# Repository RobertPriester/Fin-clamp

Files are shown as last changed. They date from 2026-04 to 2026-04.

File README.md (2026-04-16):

# Juvenile Fin-Clamp: Open hardware designs, sensor processing scripts and CFD resources for minimally invasive biologging of juvenile sharks

This repository contains all hardware design files, sensor processing scripts, 
and computational fluid dynamics (CFD) resources associated with the following publication:

> Citation and DOI to be added upon publication.

## Repository Structure

### 🗂️ Fin-clamp production
Resources to reproduce the Juvenile Fin-Clamp hardware.
- **CAD resources** — CAD files in .step (universal) and .f3z (Fusion 360) formats
- **Instructions** — Step-by-step production instructions, PDF technical plans and assembly resources

### 📊 Sensor processing scripts
R scripts for processing LittleLeonardo accelerometry, depth and temperature data 
to reproduce the results of the publication. Includes an R script adapted from the 
MATLAB code of Cade et al. (2018) to run jiggle method calculations.

### 🌊 CFD
Resources for the computational fluid dynamics simulations.
- **3D models** — Simplified .stl models of the Juvenile Fin-Clamp and juvenile 
  smooth hammerhead shark used in SimScale simulations
- **Simulation results** — SimScale simulation outputs, summary table, and R scripts 
  for processing results and producing figures

## Authors

C. Robert Priester, Jorge Fontes, Fred Buyle, Diya Das, Bruno C. L. Macena, 
Colin Simpfendorfer, Esben Moland Olsen, Pedro Afonso

## Software Requirements

### R Scripts
The sensor processing and CFD result scripts were developed in R. We recommend 
using a recent version of R (≥ 4.0) and RStudio. Required packages are listed 
at the top of each script. The jiggle method script is adapted from the original 
MATLAB code of Cade et al. (2018) for use in R.

> Cade, D.E., Barr, K.R., Calambokidis, J., Friedlaender, A.S. and Goldbogen, J.A. 
> (2018). Determining forward speed from accelerometer jiggle in aquatic 
> environments. Journal of Experimental Biology, 221(2).

### CFD Simulations
Simulations were run using [SimScale](https://www.simscale.com/), a web-based 
CFD platform. The .stl files in the /CFD/3D models folder can be imported 
directly into SimScale to reproduce or modify the simulations.

## Data Availability

Raw tag data used and analyzed in this study are not publicly archived due to 
ongoing research but are available from the corresponding author upon reasonable 
request.

## License

Hardware design files (CAD, production files): CERN Open Hardware Licence v2 - Strongly Reciprocal (CERN-OHL-S v2) 
Documentation and instructions: Creative Commons Attribution 4.0 International (CC BY 4.0)

## Contact

**C. Robert Priester** (corresponding author)
robert.priester@posteo.de

For questions related to fin-clamp development and contributions, please use 
the [GitHub Issues](../../issues) function of this repository.

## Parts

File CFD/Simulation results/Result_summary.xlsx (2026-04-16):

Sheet: Meta
Run | Shark_size | Weight | Tag/Shark_weight | Tag/shark_area | Tag | Tag_weight | Tag_frontal_area | Velocity | Ref_area | Cells | Quality | Iteration
120_0.5_NA | 1.2 | 8470.56 | 1.2% | 10.9% | NO | 100 | 0.00157084 | 0.5 | 0.01446 | 6110226 | 0.576 | 2000
120_0.5_T | 1.2 | 8470.56 | 1.2% | 10.9% | YES | 100 | 0.00157084 | 0.5 | 0.01446 | 3933008 | 0.384 | 2000
80_1_NA | 0.8 | 2624.27 | 3.8% | 16.3% | NO | 100 | 0.00157084 | 1 | 0.00964 | 5966981 | 0.585 | 2000
100_1_NA | 1 | 5001.24 | 2.0% | 13.0% | NO | 100 | 0.00157084 | 1 | 0.01205 | 6742979 | 0.556 | 2000
120_1_NA | 1.2 | 8470.56 | 1.2% | 10.9% | NO | 100 | 0.00157084 | 1 | 0.01446 | 6110393 | 0.576 | 2000
160_1_NA | 1.6 | 19452.92 | 0.5% | 8.2% | NO | 100 | 0.00157084 | 1 | 0.01927 | 4154136 | 0.501 | 2000
80_1_T | 0.8 | 2624.27 | 3.8% | 16.3% | YES | 100 | 0.00157084 | 1 | 0.00964 | 4520569 | 0.494 | 2000
100_1_T | 1 | 5001.24 | 2.0% | 13.0% | YES | 100 | 0.00157084 | 1 | 0.01205 | 4726084 | 0.502 | 2000
120_1_T | 1.2 | 8470.56 | 1.2% | 10.9% | YES | 100 | 0.00157084 | 1 | 0.01446 | 3934513 | 0.389 | 2000
160_1_T | 1.6 | 19452.92 | 0.5% | 8.2% | YES | 100 | 0.00157084 | 1 | 0.01927 | 3469121 | 0.417 | 2000
80_2.5_NA | 0.8 | 2624.27 | 3.8% | 16.3% | NO | 100 | 0.00157084 | 2.5 | 0.00964 | 5966851 | 0.583 | 2000
120_2.5_NA | 1.2 | 8470.56 | 1.2% | 10.9% | NO | 100 | 0.00157084 | 2.5 | 0.01446 | 6110393 | 0.576 | 2000
160_2.5_NA | 1.6 | 19452.92 | 0.5% | 8.2% | NO | 100 | 0.00157084 | 2.5 | 0.01927 | 4154136 | 0.501 | 2000
80_2.5_T | 0.8 | 2624.27 | 3.8% | 16.3% | YES | 100 | 0.00157084 | 2.5 | 0.00964 | 4520569 | 0.494 | 2000
120_2.5_T | 1.2 | 8470.56 | 1.2% | 10.9% | YES | 100 | 0.00157084 | 2.5 | 0.01446 | 3934513 | 0.389 | 2000
160_2.5_T | 1.6 | 19452.92 | 0.5% | 8.2% | YES | 100 | 0.00157084 | 2.5 | 0.01927 | 3469121 | 0.417 | 2000

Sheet: Simulations
Run | Shark size | Weight | Tag/Shark weight | Tag/shark area | Tag | Tag weight | Tag frontal area | Velocity(m/s) | Reference area | Cells | Quality | Iteration | PRESSURE_FORCE_X | PRESSURE_FORCE_Y | PRESSURE_FORCE_Z | TOTAL_FORCE_X | TOTAL_FORCE_Y | TOTAL_FORCE_Z | VISCOUS_FORCE_X | VISCOUS_FORCE_Y | VISCOUS_FORCE_Z | Delta_Total_X |  | Delta_power | Metabolic_energy_W | Metabolic_energy_J | Daily_energy_penalty
120_0.5_NA | 1.2 | 8470.56 | 1.2% | 10.9% | NO | 105 | 0.00157084 | 0.5 | 0.01446 | 6110226 | 0.576 | 2000 | 0.40 | 0.05 | 1.89 | 0.71 | 0.05 | 1.87 | 0.31 | 0.002039952769 | -0.02 | 0.04 | 5.58%
120_0.5_T | 1.2 | 8470.56 | 1.2% | 10.9% | YES | 105 | 0.00157084 | 0.5 | 0.01446 | 3933008 | 0.384 | 2000 | 0.44 | 0.14 | 1.91 | 0.75 | 0.14 | 1.89 | 0.31 | 0.0005188760977 | -0.02
80_1_NA | 0.8 | 2624.27 | 4.0% | 16.3% | NO | 105 | 0.00157084 | 1 | 0.00964 | 5966981 | 0.585 | 2000 | 0.70 | 0.07 | 3.42 | 1.22 | 0.07 | 3.38 | 0.52 | 0.001136633648 | -0.04 | 5.8440 | 477.74%
100_1_NA | 1 | 5001.24 | 2.1% | 13.0% | NO | 105 | 0.00157084 | 1 | 0.01205 | 6742979 | 0.556 | 2000 | 1.03 | -0.06 | 5.53 | 1.83 | -0.06 | 5.47 | 0.80 | 0.002823207532 | -0.06
120_1_NA | 1.2 | 8470.56 | 1.2% | 10.9% | NO | 105 | 0.00157084 | 1 | 0.01446 | 6110393 | 0.576 | 2000 | 1.55 | 0.23 | 7.87 | 2.67 | 0.23 | 7.78 | 1.12 | 0.01 | -0.09 | 12.7556 | 478.30%
160_1_NA | 1.6 | 19452.92 | 0.5% | 8.2% | NO | 105 | 0.00157084 | 1 | 0.01927 | 4154136 | 0.501 | 2000 | 2.60 | -0.01 | 14.16 | 4.53 | -0.0009062607321 | 14.01 | 1.94 | 0.01 | -0.15 | 21.6252 | 477.07%
80_1_T | 0.8 | 2624.27 | 4.0% | 16.3% | YES | 105 | 0.00157084 | 1 | 0.00964 | 4520569 | 0.494 | 2000 | 1.02 | 0.56 | 3.42 | 1.56 | 0.56 | 3.38 | 0.53 | -0.001440980359 | -0.04 | 0.3323 | 27.16% | 0.3322642967 | 1.329057187 | 4784.605872 | 114.8 | -0.5660293074 | -0.09691001301
100_1_T | 1 | 5001.24 | 2.1% | 13.0% | YES | 105 | 0.00157084 | 1 | 0.01205 | 4726084 | 0.502 | 2000 | 1.42 | 0.60 | 5.51 | 2.21 | 0.60 | 5.45 | 0.78 | -0.00194117961 | -0.06 | 0.3813 | 20.87%
120_1_T | 1.2 | 8470.56 | 1.2% | 10.9% | YES | 105 | 0.00157084 | 1 | 0.01446 | 3934513 | 0.389 | 2000 | 1.71 | 0.54 | 7.86 | 2.82 | 0.54 | 7.77 | 1.11 | -0.0005802425074 | -0.09 | 0.1564 | 5.87% | 0.1564333467 | 0.6257333866 | 2252.640192 | 54.1 | -1.231669021 | 0.07918124605
160_1_T | 1.6 | 19452.92 | 0.5% | 8.2% | YES | 105 | 0.00157084 | 1 | 0.01927 | 3469121 | 0.417 | 2000 | 2.82 | 0.74 | 14.13 | 4.73 | 0.74 | 13.97 | 1.91 | 0.01 | -0.16 | 0.2021 | 4.46% | 0.2021191677 | 0.808476671 | 2910.516016 | 69.9 | -1.350765638 | 0.2041199827
80_2.5_NA | 0.8 | 2624.27 | 4.0% | 16.3% | NO | 105 | 0.00157084 | 2.5 | 0.00964 | 5966851 | 0.583 | 2000 | 4.17 | 0.64 | 22.20 | 7.07 | 0.64 | 21.98 | 2.89 | 0.003504137696 | -0.22 | 7.66 | 492.17%
120_2.5_NA | 1.2 | 8470.56 | 1.2% | 10.9% | NO | 105 | 0.00157084 | 2.5 | 0.01446 | 6110393 | 0.576 | 2000 | 9.28 | 1.96 | 50.73 | 15.42 | 1.98 | 50.26 | 6.14 | 0.02 | -0.47 | 13.54 | 479.72%
160_2.5_NA | 1.6 | 19452.92 | 0.5% | 8.2% | NO | 105 | 0.00157084 | 2.5 | 0.01927 | 4154136 | 0.501 | 2000 | 15.68 | -0.15 | 90.19 | 26.16 | -0.12 | 89.41 | 10.48 | 0.03 | -0.77 | 22.63 | 478.00%
80_2.5_T | 0.8 | 2624.27 | 4.0% | 16.3% | YES | 105 | 0.00157084 | 2.5 | 0.00964 | 4520569 | 0.494 | 2000 | 6.25 | 3.41 | 21.86 | 9.21 | 3.40 | 21.63 | 2.96 | -0.01 | -0.22 | 2.1441 | 30.34% | 5.360261068 | 21.44104427 | 77187.75938 | 1852.5
120_2.5_T | 1.2 | 8470.56 | 1.2% | 10.9% | YES | 105 | 0.00157084 | 2.5 | 0.01446 | 3934513 | 0.389 | 2000 | 10.31 | 3.42 | 50.33 | 16.37 | 3.41 | 49.86 | 6.06 | -0.01 | -0.47 | 0.9446 | 6.12% | 2.361517566 | 9.446070262 | 34005.85294 | 816.1
160_2.5_T | 1.6 | 19452.92 | 0.5% | 8.2% | YES | 105 | 0.00157084 | 2.5 | 0.01927 | 3469121 | 0.417 | 2000 | 17.05 | 3.96 | 89.98 | 27.37 | 3.98 | 89.15 | 10.32 | 0.02 | -0.83 | 1.2103 | 4.63% | 3.02571437 | 12.10285748 | 43570.28693 | 1045.7
 |  |  |  |  |  |  |  |  |  |  |  |  |  |  |  |  |  |  |  |  |  |  |  |  | 111.6935848601%
 |  |  |  |  |  |  |  |  |  |  |  |  |  |  |  |  |  |  |  |  |  |  |  |  | 103.7644536316%

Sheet: Mesh dependancy
Run | Input mesh | Shark size | Tag | Velocity(m/s) | Algorithm | Fineness | Volumes | Nodes | Max NonO | Quality score | PRESSURE_FORCE_X | PRESSURE_FORCE_Y | PRESSURE_FORCE_Z | TOTAL_FORCE_X | TOTAL_FORCE_Y | TOTAL_FORCE_Z | VISCOUS_FORCE_X | VISCOUS_FORCE_Y | VISCOUS_FORCE_Z | Column1
Pre | Remodelled251023_remeshed_reducedIII | 80 | NO | 1 | Hex | Fine | 1540100 | 2088741 | 87.97 | 0.46 | 0.90 | -0.23 | 3.27 | 1.45 | -0.23 | 3.24 | 0.55 | 0.0006168922828 | -0.04
Pre | Remodelled241030_reduced50 | 80 | NO | 1 | Hex | Moderate | 1979896 | 2376287 | 87.85 | 0.52 | 1.09 | 0.04 | 3.58 | 1.65 | 0.04 | 3.55 | 0.56 | 0.002417378538 | -0.03
Pre | Remodelled251023_remeshed_reducedIII | 80 | NO | 1 | Standard | 5 | 3555913 | 989374 | 89.1 |  | 0.95 | -0.09 | 3.64 | 1.46 | -0.09 | 3.61 | 0.51 | 0.0006941273648 | -0.03
Pre | Remodelled241030_reduced50 | 80 | NO | 1 | Hex | Fine | 4103420 | 4852123 | 85.7 | 0.54 | 0.89 | -0.02 | 3.72 | 1.44 | -0.02 | 3.69 | 0.54 | 0.001064137875 | -0.04
Manual | Remodelled241030_reduced50 | 80 | NO | 1 | Hex | Manual (0.5) | 7657633 | 10124840 | 86.56 | 0.59 | 0.71 | 0.01 | 3.38 | 1.23 | 0.01 | 3.34 | 0.52 | 0.002300590639 | -0.04 | 0.00
Manual | Remodelled241030_reduced50 | 80 | NO | 1 | Hex | Manual (0.65) | 5966981 | 7764503 | 85.44 | 0.59 | 0.70 | 0.07 | 3.42 | 1.22 | 0.07 | 3.38 | 0.52 | 0.001136321584 | -0.04 | 0.01
Manual | Remodelled241030_reduced50 | 80 | NO | 1 | Hex | Manual (0.725) | 2995024 | 3872601 | 87.35 | 0.5 | 0.73 | -0.04 | 3.46 | 1.25 | -0.03 | 3.42 | 0.52 | 0.002223197654 | -0.04 | -0.02
Manual | Remodelled241030_reduced50 | 80 | NO | 1 | Hex | Manual (5) | 1253214 | 1445283 | 87.11 | 0.61 | 1.14 | 0.01 | 3.40 | 1.66 | 0.01 | 3.38 | 0.52 | 0.0008462221316 | -0.02 | -0.42
Manual | Remodelled241030_reduced50 | 80 | NO | 1 | Hex | Manual (12) | 643259 | 728039 | 87.38 | 0.64 | 1.63 | -0.14 | 3.89 | 2.14 | -0.14 | 3.86 | 0.51 | -0.0006558393983 | -0.03 | -0.49
Manual | Remodelled241030_reduced50 | 80 | NO | 1 | Hex | Manual (15) | 394268 | 468042 | 87.53 | 0.57 | 1.42 | 0.01 | 2.88 | 1.89 | 0.02 | 2.86 | 0.47 | 0.004983145064 | -0.02 | 0.21

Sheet: Sheet1
Run | Shark size | Tag | Velocity(m/s) | Vol_Xfront | Vol_Xback | Vol_Y | Vol_Z | Reference length | Reference area |  |  | Scaling
1 | 0.8 | NO | 1 | 4 | 8 | 1.1 | 1.1 | 0.8 | 0.009637 |  |  |  | TL | Cephalofoil | Ratio
4 | 0.8 | YES | 1 | 4 | 8 | 1.1 | 1.1 | 0.8 | 0.01204625
7 | 0.8 | NO | 3 | 4 | 8 | 1.1 | 1.1 | 0.8 | 0.0144555 |  | 592.7 | 800 | 125.8 | 34.3 | 0.2726550079
10 | 0.8 | YES | 3 | 4 | 8 | 1.1 | 1.1 | 0.8 | 0.019274 |  | Scaling original to 800 | 1.350
 | 1 | YES | 1 | 5 | 10 | 1.4 | 1.4 | 1 |  |  | 100 | 1.687
 | 1 | NO | 2 | 5 | 10 | 1.4 | 1.4 | 1 |  |  | Scaling 120 | 2.02
2 | 1.2 | NO | 1 | 6 | 12 | 1.6 | 1.6 | 1.2 |  |  | Scaling 160 | 2.70
5 | 1.2 | YES | 1 | 6 | 12 | 1.6 | 1.6 | 1.2 | 0.020362393
8 | 1.2 | NO | 3 | 6 | 12 | 1.6 | 1.6 | 1.2
11 | 1.2 | YES | 3 | 6 | 12 | 1.6 | 1.6 | 1.2
3 | 1.6 | NO | 1 | 8 | 16 | 2.2 | 2.2 | 1.6 | 0.020362393
6 | 1.6 | YES | 1 | 8 | 16 | 2.2 | 2.2 | 1.6
9 | 1.6 | NO | 3 | 8 | 16 | 2.2 | 2.2 | 1.6
12 | 1.6 | YES | 3 | 8 | 16 | 2.2 | 2.2 | 1.6
 |  |  |  |  |  |  |  |  |  |  |  |  |  |  | Tag
 |  |  |  |  |  |  |  |  |  |  |  |  |  |  | 160 | 1088.393 | 0.001088393
 |  |  |  |  |  |  |  |  |  | 0.01951138856

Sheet: Parameters
Parameter | Value
Fluid density | 1024.065

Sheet: Simulations_old
Run | Shark size | Tag | Velocity(m/s) | Reference area | FORCE_COEFFICIENT_CD | FORCE_COEFFICIENT_CL | FORCE_COEFFICIENT_CLF | FORCE_COEFFICIENT_CLR | FORCE_COEFFICIENT_CM | PRESSURE_FORCE_X | PRESSURE_FORCE_Y | PRESSURE_FORCE_Z | TOTAL_FORCE_X | TOTAL_FORCE_Y | TOTAL_FORCE_Z | VISCOUS_FORCE_X | VISCOUS_FORCE_Y | VISCOUS_FORCE_Z
1 | 0.8 | NO | 1 | 0.00964 | 0.2916 | 0.7471115996 | 0.6015446181 | 0.1455669816 | 0.2279888183 | 0.8948119138 | -0.01744674042 | 3.722515185 | 1.438907042 | -0.01638260255 | 3.686590214 | 0.5440951283 | 0.001064137875 | -0.03592497111
2 | 1.2 | NO | 1 | 0.01446 | 0.4308 | 1.101435767 |  |  |  | 2.052635583 | 0.3774924426 | 8.22297731 | 3.188948982 | 0.3780421683 | 8.152481484 | 1.136313399 | 0.0005497257511 | -0.07049582589
3 | 1.6 | NO | 1 | 0.01927 | 0.5942 | 1.465776235 | 1.342594183 | 0.1231820523 | 0.6097060652 | 3.910710965 | -0.3427849427 | 14.57959546 | 5.864477637 | -0.3422436144 | 14.4656202 | 1.953766672 | 0.000541328335 | -0.113975258
4 | 0.8 | YES | 1 | 0.00964
5 | 1.2 | YES | 1 | 0.01446 | 0.5670 | 1.071733436 | 0.8654846665 | 0.2062487697 | 0.3296179484 | 3.05570257 | 1.026039793 | 8.005983751 | 4.196462266 | 1.010611627 | 7.93263416 | 1.140759696 | -0.0154281666 | -0.07334959065
6 | 1.6 | YES | 1 | 0.01927 | 0.6156 | 1.383486083 | 1.125968181 | 0.2575179025 | 0.4342251391 | 4.469666599 | 0.268321942 | 14.54912211 | 6.41815785 | 0.2657038639 | 14.42451228 | 1.948491251 | -0.002618078059 | -0.1246098372
7 | 0.8 | NO | 3 | 0.00964 | 0.2671 |  |  |  |  | 7.749350384 | 0.01819096524 | 34.8508484 | 11.85994343 | 0.01888801854 | 34.5879375 | 4.110593048 | 0.0006970532972 | -0.2629109011
8 | 1.2 | NO | 3 | 0.01446 | 0.4025 |  |  |  |  | 18.364295 | 3.585761721 | 76.81726542 | 26.81330065 | 3.578321586 | 76.31019117 | 8.449005651 | -0.0074401347 | -0.5070742495
9 | 1.6 | NO | 3 | 0.01927 | 0.5571 |  |  |  |  | 35.50694312 | -1.850076438 | 134.378032 | 49.48106837 | -1.85074291 | 133.5822111 | 13.97412525 | -0.0006664724264 | -0.7958209627
10 | 0.8 | YES | 3 | 0.00964
11 | 1.2 | YES | 3 | 0.01446 | 0.5500
12 | 1.6 | YES | 3 | 0.01927 | 0.5816 | 1.420499191 | 1.157580522 | 0.2629186688 | 0.4473309265 | 40.64423763 | 3.097063999 | 134.1475888 | 54.57843623 | 3.075306555 | 133.2937674 | 13.9341986 | -0.02175744412 | -0.8538213812

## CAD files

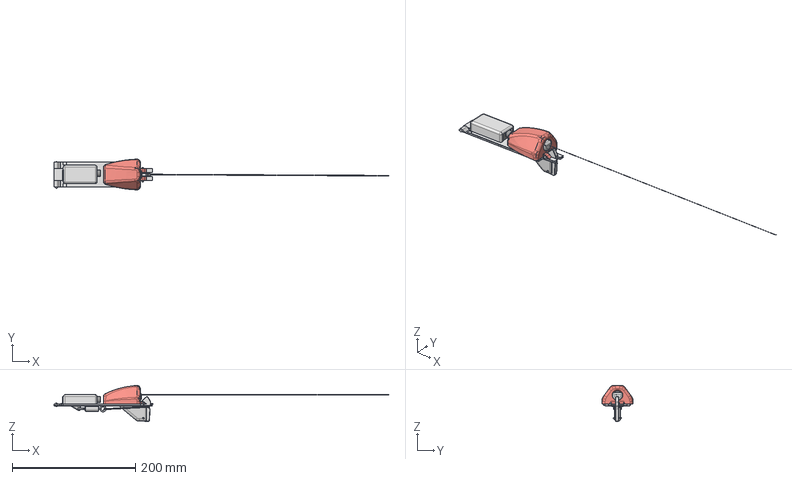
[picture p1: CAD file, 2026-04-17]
Fin-clamp construction/CAD resources/Assembled tag.step
543.3 x 49.9 x 58.4 mm

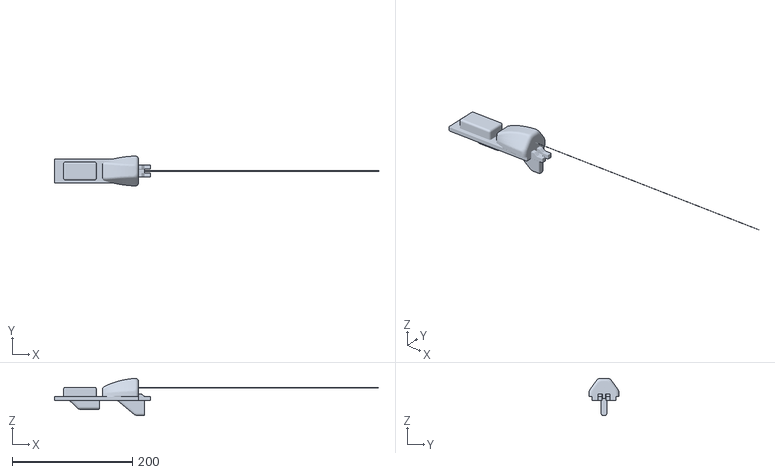
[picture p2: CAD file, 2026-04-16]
CFD/3D models/Fin-clamp_simplified.stl
540.0 x 49.9 x 61.9

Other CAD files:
Fin-clamp construction/CAD resources/Assembled tag.f3z

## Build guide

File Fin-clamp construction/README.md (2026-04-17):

# Juvenile Fin-Clamp — Production Resources

This folder contains all resources necessary to reproduce the Juvenile Fin-Clamp 
described in:

> Citation and DOI to be added upon publication.

## Contents

- **/CAD resources** — CAD files in .step (universal) and .f3z (Fusion 360) 
  formats for all fin-clamp components and exported CAD plans
- **Fin-Clamp Construction Instructions** — Step-by-step production instructions, PDF technical plans, 
  and all relevant assembly resources

## Contributors

Design and documentation: C. Robert Priester, Catarina Fazenda

## How to Reproduce the Fin-Clamp

Full step-by-step instructions are provided in the Fin-Clamp Construction Instructions document
with all necessary technical plans and resources.
For questions about specific production steps, please open a 
[GitHub Issue](../issues) (see below).

## Contributing — We Welcome Your Input!

The Juvenile Fin-Clamp is designed as an evolving, community-driven open 
hardware tool. We actively encourage researchers who use, test, or modify 
the design to share their experiences and suggestions.

### How to contribute:
- **Report a problem** — If you encounter issues during production or deployment, 
  open a [GitHub Issue](../issues) describing the problem
- **Suggest an improvement** — Have an idea for a design improvement or 
  adaptation for a different species or fin type? Open an Issue and describe 
  your suggestion
- **Share your results** — Used the fin-clamp in your research? We would love 
  to hear about it — open an Issue or get in touch directly

Your contributions help improve this tool for the entire research community.

## License

Creative Commons Attribution–NonCommercial–ShareAlike 4.0 International 
([CC BY-NC-SA 4.0](https://creativecommons.org/licenses/by-nc-sa/4.0/))

By contributing to this repository, you agree that your contributions will be 
shared under the same license.

## Contact

**C. Robert Priester**
robert.priester@posteo.de

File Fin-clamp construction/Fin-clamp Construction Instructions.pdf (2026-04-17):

# FIN-CLAMP CONSTRUCTION

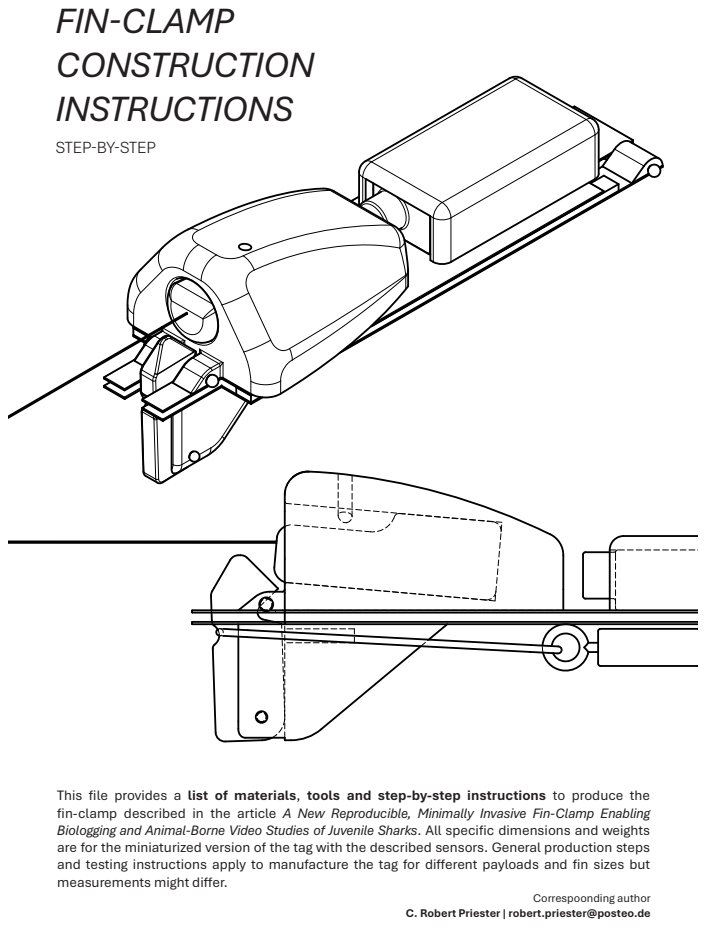
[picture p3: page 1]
INSTRUCTIONS; Correspoonding author

STEP-BY-STEP

This file provides a list of materials, tools and step-by-step instructions to produce the
fin-clamp described in the article A New Reproducible, Minimally Invasive Fin-Clamp Enabling
Biologging and Animal-Borne Video Studies of Juvenile Sharks. All specific dimensions and weights
are for the miniaturized version of the tag with the described sensors. General production steps
and testing instructions apply to manufacture the tag for different payloads and fin sizes but
measurements might differ.

C. Robert Priester | robert.priester@posteo.de

## Contents

## Overview

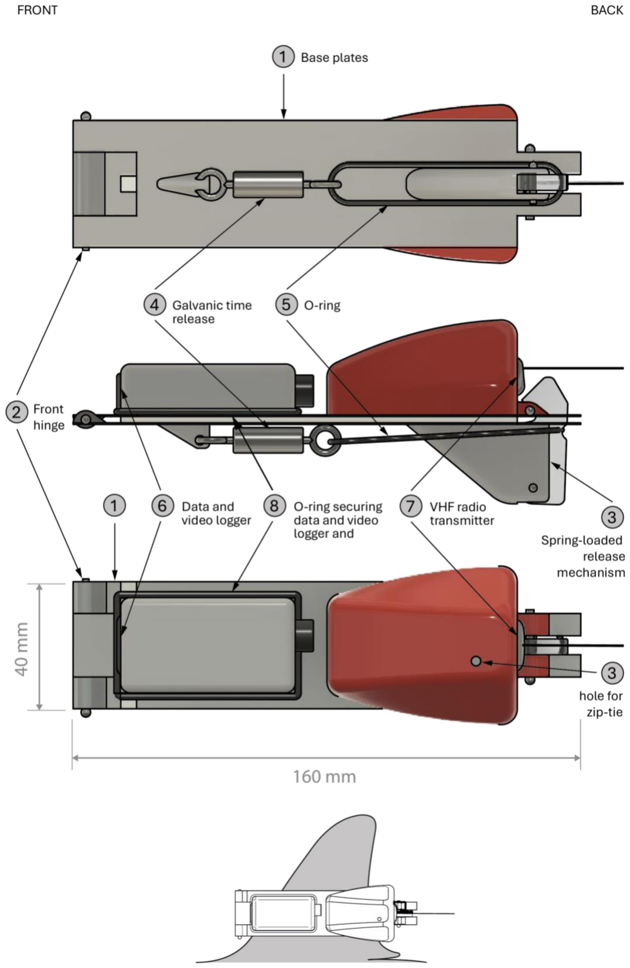
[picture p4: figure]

## Material

Description | Quantity | Dimensions | Comments
Carbon fiber sheet | 1 | 200 x 100 x 5 mm | Determines flex of clamp – thicker for larger fins and clamps
Ballpoint pen | 2 | | Inside tube for hinge hole
Ballpoint pen spring | 1 | | Or alternatively a stainless-steel spring of similar size
Long stainless-steel rivet | 1 | >45 mm long | For hinge
Short stainless-steel rivets | 2 | 2 mm diameter | Different diameter or aluminum alloy also possible
Marine grade epoxy + hardener | 100 g
Fiberglass shreds/ Fiberglass mat | 10 g | | If shreds are not available but a small fiberglass mat and cut it into ca. 1cm short strands
HCP foam | 1 | Min. 125 x 50 x 35 mm
Syntactic foam | 1 | Min. 50 x 50 x 10 mm
Sand | 20 g | | Grain size determines coat coarseness
Cyanoacrylate glue | 10 g
Rubbing alcohol | 100 ml
Acrylic spray paint | 2 | | 1 neutral color (grey), 1 signal color
Clear coat spray | 1
Reflective tape | <1 m

## Tools

- Saw (fine toothed metal/composite saw best)
- Sandpaper (60, 100, 150 grit)
- Narrow flat metal file
- Pliers
- Masking tape
- Mixing cup
- Mixing stick
- Brush
- Carpet knife
- Paper wipes (best lint-free)

- Tape measure
- Calipers
- Power drill
- Metal drill bits (2, 2.5, 3, 17 mm) Optional
- Dremel or similar precision drill
- Oven
- Round file
- Crimping pliers
- Angle grinder
- Precision scale

## Step-by-step instructions

## Base plates

1) Cut fiberglass bases
a) Cut two rectangular bases 40 x 165 mm from sheet
(i) (Study species fin size + 40 mm)
b) Mark front and back, and sensor and release side
c) Mark longitudinal middle line

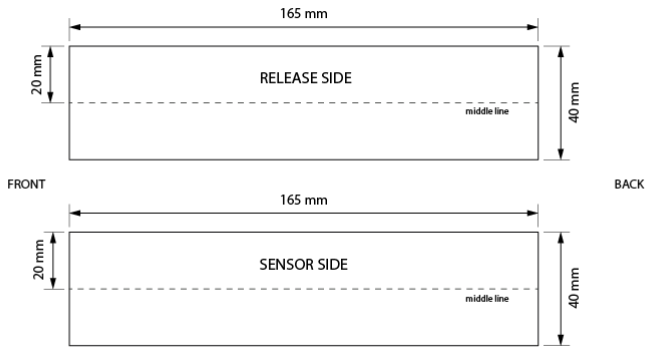
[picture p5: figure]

Figure 1
2) Make hinge
a) Prepare front surface (front 20 mm of both bases)
i) Sand with 100 grit
ii) Clean with rubbing alcohol and wipes
b) Mark line 10 mm from front edge (see Figure 2)
c) Place ballpoint pen inner tube on line and fix in place using tape outside of the base area
d) Cover with fiber-reinforced epoxy resin (remove bubbles). Tube must be completely covered with >2 mm layer
e) Cure in oven
f) If necessary, sand, clean and repeat steps 2d) and 2e), until achieving even required thickness g) Remove tube (slowly twist and pull)

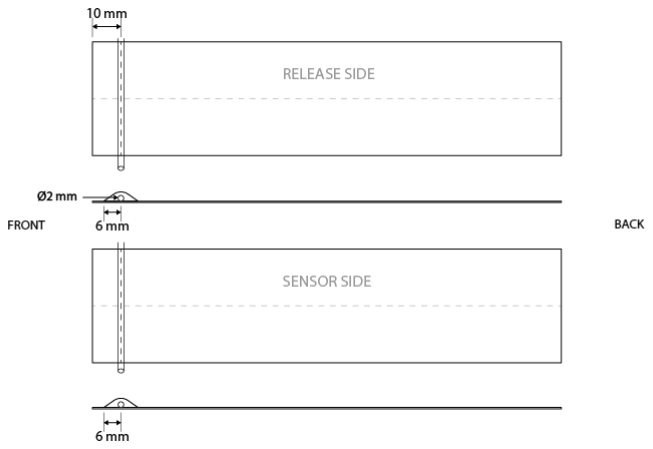
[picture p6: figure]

Figure 2
h) Sand excess resin until smooth and flush with sides of the base
i) Cut 5 mm at the front (see Figure 3)
j) Test fit of long rivet – drill hole wider if necessary

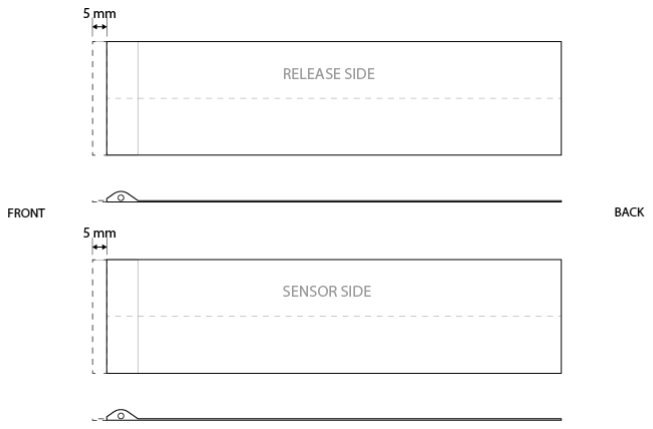
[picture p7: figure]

Figure 3
3) Cut hinge
a) On Sensor Base, remove 20 x 10 mm rectangles on both sides of the cured hinge (see Figure 4 top)
b) On the Release Base, remove a 20 x 20 mm square in the middle of the cured hinge (see Figure 5 bottom)
c) Test that both sheets fit into each other and hinge moves freely

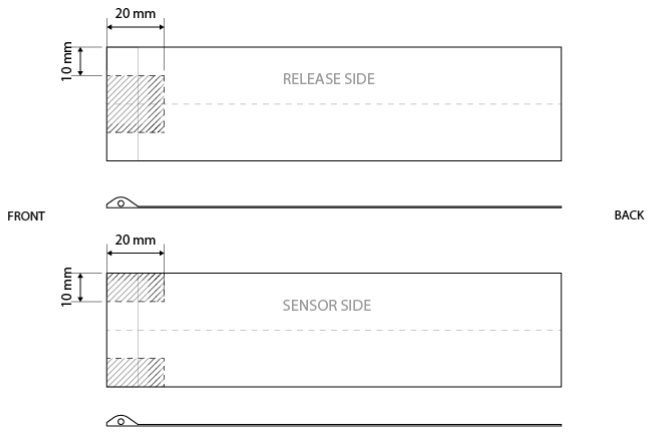
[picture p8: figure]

Figure 4
4) Cut release flaps
a) Remove a 20 x 10 mm rectangle on both sides of the back end of the Release and Sensor Base (see Figure 5)
b) Remove a 20 x 6 mm rectangle centered on the middle on the back of the Release and Sensor Base

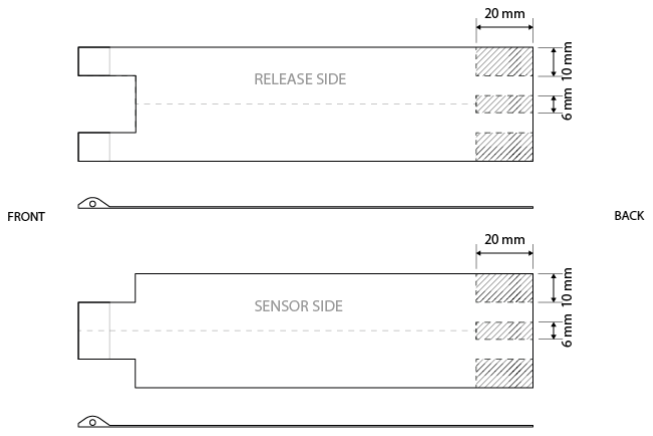
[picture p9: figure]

Figure 5
5) Inside coating
a) Cut 3 strips of HCP foam (125 x 5 x 2 mm)
b) Prepare the inside surface of both Bases
i) Sand with 100 grit
ii) Clean with rubbing alcohol and wipes
c) Cover the inside surfaces of both Bases with thin layer of resin (brush on)
d) Glue two strips flush with outside edge of the inside release sheet (see Figure 6 top)
e) Glue one strip to along middle line of inside sensor sheet (see Figure 6 bottom)
f) Sprinkle sand on remaining exposed resin before cured
g) Place in oven (50 °C) until fully cured

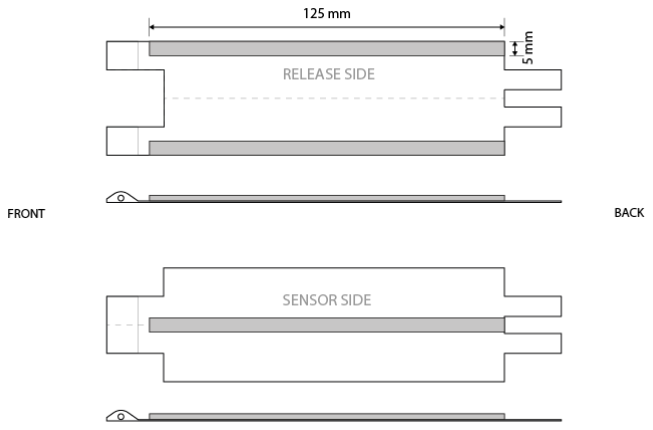
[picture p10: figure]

Figure 6

## Components

1) Sensor foam
(DVL400M028—VD3GT, Little Leonardo specific specifications)
a) Cover sensor or dummy in one to two wraps of packaging tape (protecting sensor during glueing process)
b) Cut two side walls of pressure rated HCP foam (57 x 13 x 4 mm)
c) Cut one top side of pressure rated HCP foam (57 x 29 x 3 mm)

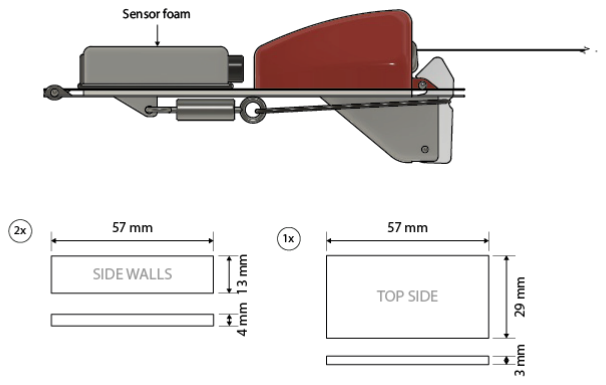
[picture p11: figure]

d) Place sensor on a flat surface and position sides and top to check confirm fit
e) If necessary, sand any walls to make sure the fit is appropriate (external overlap can be sanded after gluing)

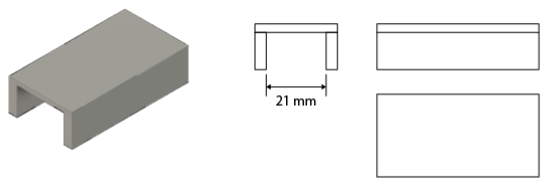
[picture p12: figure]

f) Glue walls using Cyanoacrylate glue (to assure positioning it can be glued with tape-covered sensor in place)
g) After glue has set remove sensor and round off edges and protruding corners
h) Optional: cover sensor foam in thin layer of epoxy resin
2) Release mechanism latch
a) Cut the release latch from a 5 mm polycarbonate or PVC sheet (40 x 15 mm)
b) Drill 2.5 mm hole as depicted on plan

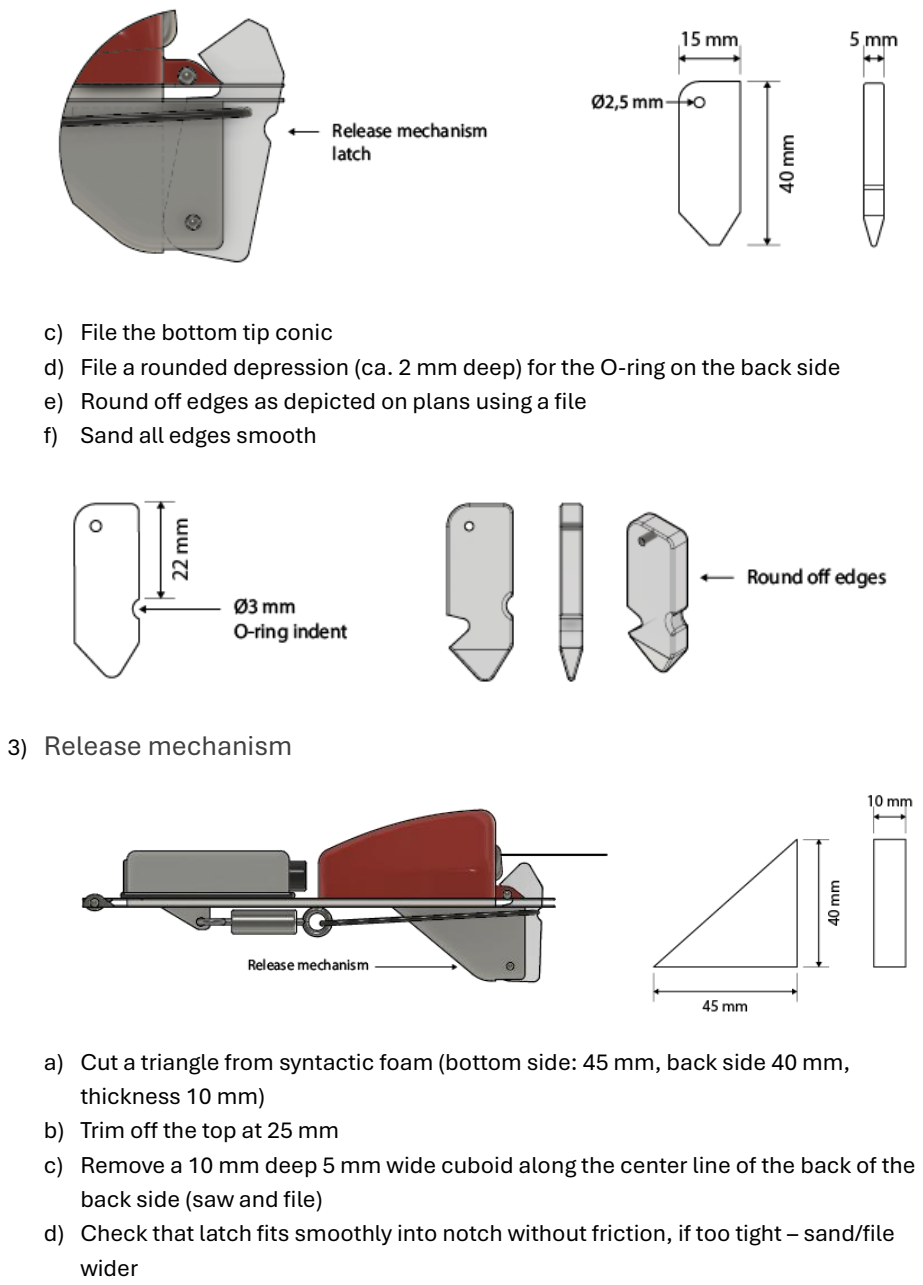
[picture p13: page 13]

c) File the bottom tip conic
d) File a rounded depression (ca. 2 mm deep) for the O-ring on the back side
e) Round off edges as depicted on plans using a file
f) Sand all edges smooth
3) Release mechanism
a) Cut a triangle from syntactic foam (bottom side: 45 mm, back side 40 mm, thickness 10 mm)
b) Trim off the top at 25 mm
c) Remove a 10 mm deep 5 mm wide cuboid along the center line of the back of the back side (saw and file)
d) Check that latch fits smoothly into notch without friction, if too tight – sand/file wider

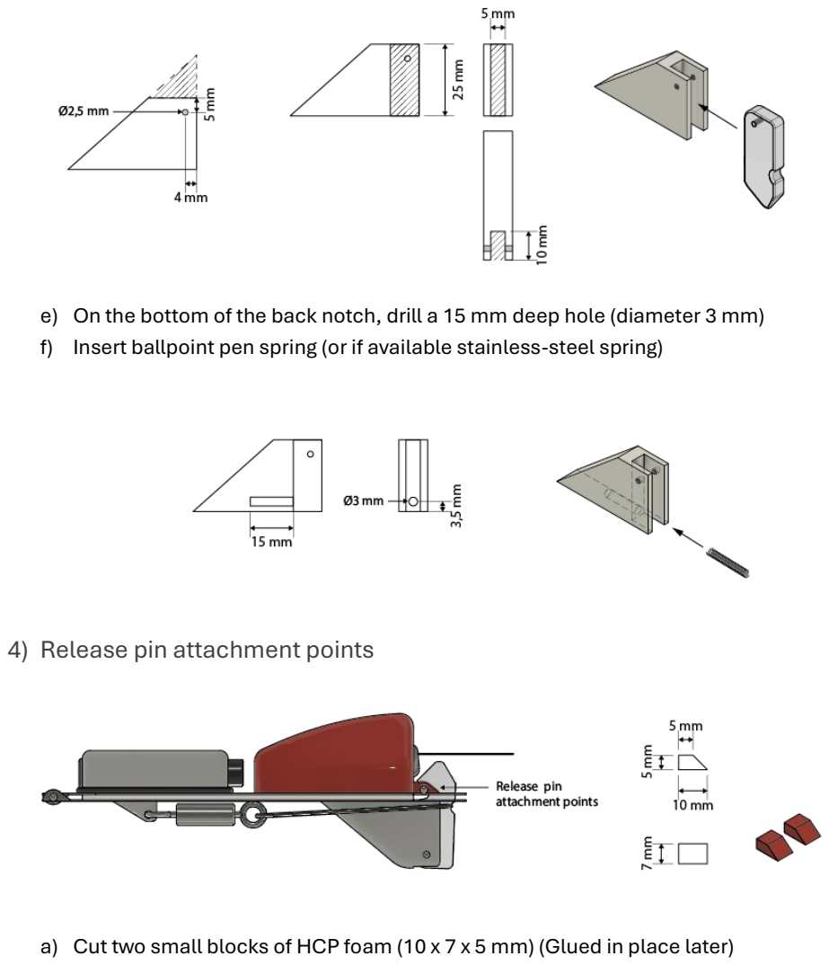
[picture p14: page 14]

e) On the bottom of the back notch, drill a 15 mm deep hole (diameter 3 mm)
f) Insert ballpoint pen spring (or if available stainless-steel spring)
4) Release pin attachment points
a) Cut two small blocks of HCP foam (10 x 7 x 5 mm) (Glued in place later)

5) GTR attachment point
a) Cut a small fin shaped triangle of syntactic foam (20 mm base, 15 mm height, 8 cm width at base)
b) Remove 5 mm from the tip
c) Smooth off edges
d) Drill hole for GTR eyelet screw (3 mm)
e) Check fit of GTR eyelet screw (bend to insert and close)
f) If GTR eyelet screw does not fit, expand hole

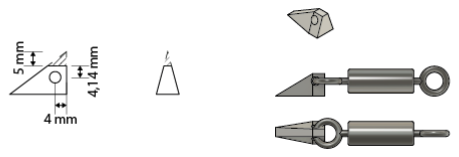
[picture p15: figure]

6) Glue first components
(Sensor foam, Release mechanism, Release pin attachment point, GTR attachment point)
a) Prepare outside surface of both bases
i) Sand with 100 grit
ii) Clean with rubbing alcohol and wipes
b) Prepare glueing surfaces of components
i) Sand with 100 grit
ii) Clean with rubbing alcohol and wipes
c) Cover glueing surfaces of components with resin
d) Place components on the respective Bases and align as shown on plans (especially the release mechanism needs to be aligned well with the middle line and the gap on the Release Base)

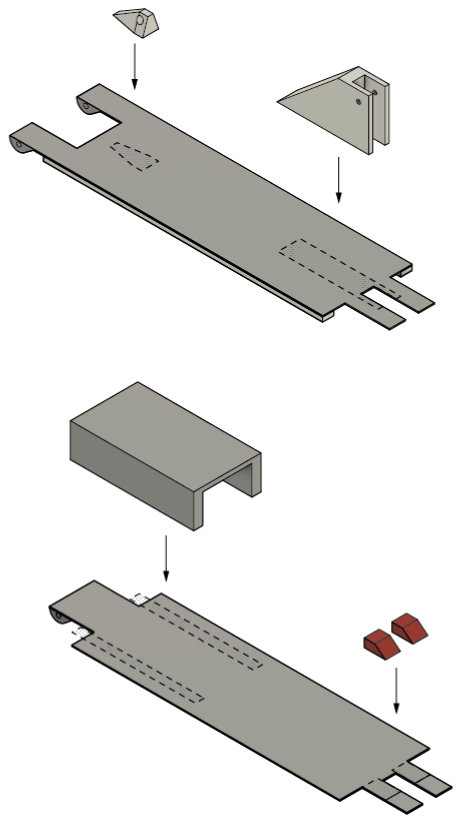
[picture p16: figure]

e) Place in oven (50 °C) until cured
7) Clean glued clamp
a) Remove excess resin with a file
b) Drill hole for release pin (3 mm)
c) Insert release pin (glue if loose)
d) Assemble main hinge pin (keep in place with tape)
8) Release latch assembly and fine-tuning
a) Insert rivet through both and cut flush b) Close both clamp sides and mark position of release pin on release latch
c) File angled notch into release latch (reference as image)
d) Test if latch keeps tag closed with assembled GTR-O-ring but springs open without. It needs to be smooth and work every time. If in doubt file more conic and use tighter O-ring

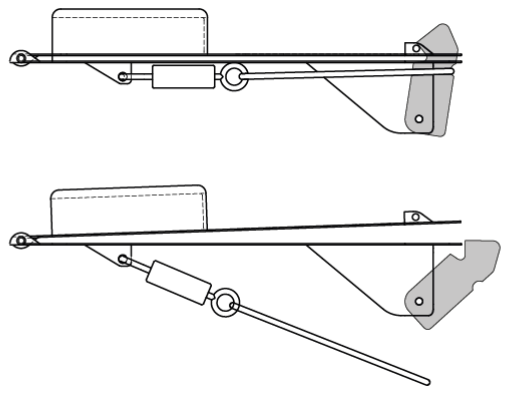
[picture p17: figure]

9) Buoyancy tests and fine-tuning
a) Test buoyancy in seawater with sensor and single GTR eyelet screw (without GTR)
b) Assembled open clamp should be slightly negative (especially release side)
c) If adjustments are necessary, sand down following components, focusing on rounded streamline forms:
i) Sensor foam
ii) Release mechanism foam
iii) GTR attachment point
iv) Inside strips

10) VHF foam
a) Cut HCP foam block (60 x 50 x 35 mm)
b) Mark VHF center point as per plans
c) Drill VHF hole using 17 mm metal drill bit at slight outward angle
d) Check fit of VHF with end protruding ca. 2 mm
i) If necessary, sand inside to improve fit – ideally VHF can be pushed in easily but does not slide out without pulling

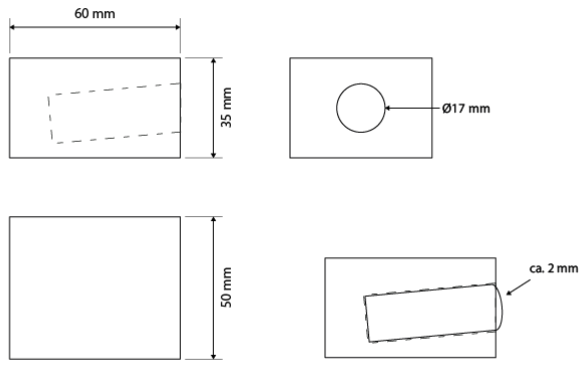
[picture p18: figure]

e) Tape to clamp in position with all components installed (GTR, Sensor, VHF) and test buoyancy
f) Reduce volume aiming for a gradual hydrodynamic shape with smooth transition from sensor foam size to larger end

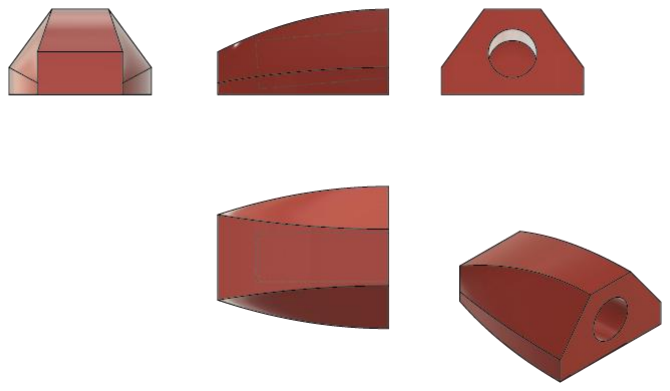
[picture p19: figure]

g) Repeat buoyancy test – buoyancy is good when tag floats upright (VHF antenna vertical) and waterline is ca. 10-15 mm below top of VHF float

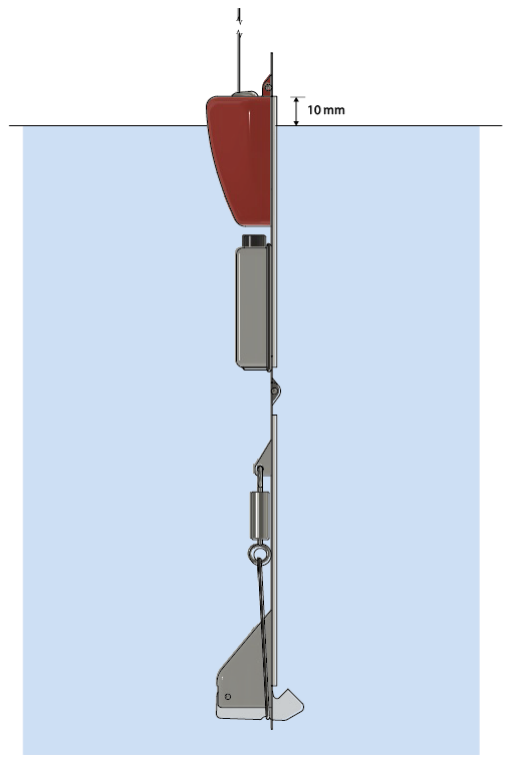
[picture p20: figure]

h) If the buoyancy is good but the position not vertical, a small piece of lead or stainless-steel metal (ex. nut) can be glued to the area close to the hinge to correct the vertical position
i) Drill a 3 mm hole on the outside part of the foam to allow the insertion of a thin zip-tie to secure the VHF

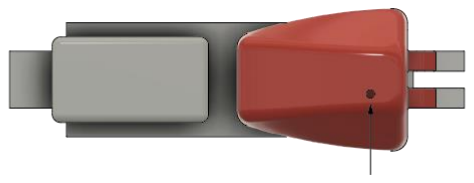
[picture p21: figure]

11) Smooth and paint
a) Once buoyancy is correct and all components are attached remove the sensor, VHF and GTR and smooth all remaining sharp edges
b) Sand all surfaces of the tag with 120 grit
c) Remove residues with rubbing alcohol and wipe clean
d) Cover inside surfaces with masking tape
e) Paint outside surfaces with neutral grey (or other paint that reduces fish interest and bites after release) and leave to dr y
f) Mask all outside surfaces except the exposed surfaces when floating
g) Paint with signal color to facilitate spotting tag at sea and leave to dry
h) Glue reflective tape to the very back of the base, that remains exposed when floating in the water
i) Write contact details on outside area of the tag
j) Cover all outside surfaces with a clear finish coat

## Full Assembly and Testing

1) Full assembly (for field tests or deployments)
k) Insert sensor into sensor foam, if too loose add one layer of tape on the sensor side until fit is tight
l) Secure sensor with 3 mm zip tie or O-ring
m) Insert VHF into VHF foam and secure by inserting a 3 mm zip-tie through hole and closing it. Double-check that VHF cannot slide out.
n) Bend open both eyelet screws of GTR
o) Insert one side into GTR attachment point and bend it closed again
p) Insert an O-ring into the other one and bend the eyelet closed again
q) Double-check that release latch moves freely and that the release mechanism spring works
r) Arm the release by tensioning the O-ring over the mechanism and the latch
s) Close the tag around the fin i) You should hear/feel the click of the release latch engaging with the release pin and the tag should be closed tightly around the fin
2) Testing
a) Re-test buoyancy with all components
b) Re-test release mechanism
i) Assemble tag with short duration GTR
ii) Clamp tag around vertical PVC sheet or similar to simulate the attachment on a dorsal fin
iii) Leave in a saltwater tank
iv) Time release and check VHF signal
c) Test VHF range

## Customization Considerations:

- The base dimensions and thickness can be changed to accommodate different payloads or allow the deployment on sharks with different fin shapes and sizes
- Wider bases provide more stability and space for payloads but are heavier requiring more floatation
- Thicker bases are stiffer and potentially better for larger and wider fins
- Foam with higher pressure rating is denser, thus larger volumes are needed to ensure buoyancy. This can affect the size and hydrodynamics of the tag and impact the minimal study animal size. We recommend using the lowest pressure rating possible for the study area and species, especially for the VHF foam. Other components can be produced from denser foam to ensure component strength (i.e. release mechanism and GTR attachment point).

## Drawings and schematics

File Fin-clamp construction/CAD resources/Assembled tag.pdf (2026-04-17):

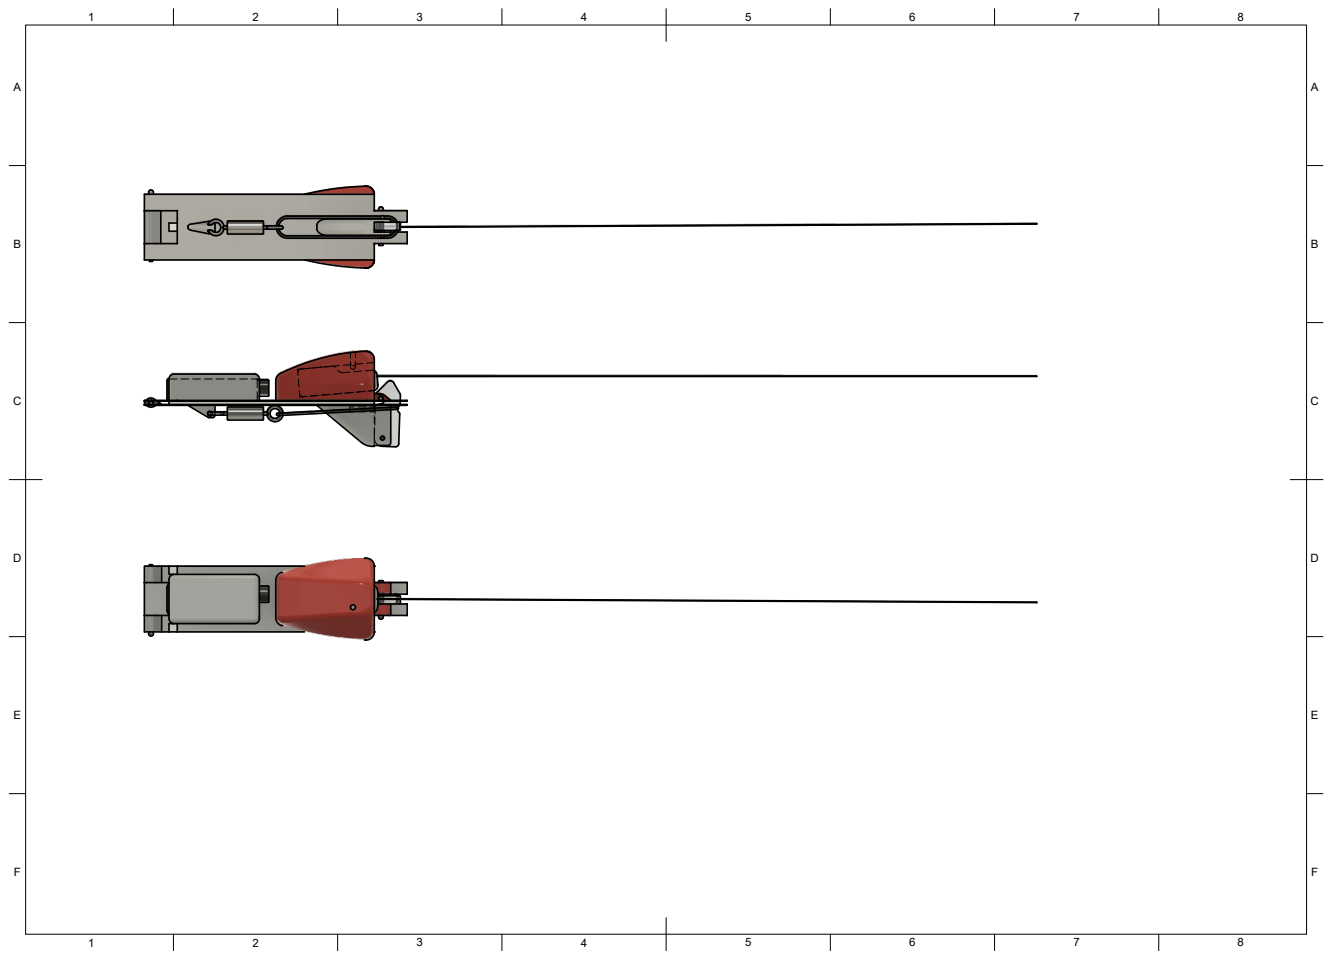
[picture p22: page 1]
8 BCDEF; ABCDEF

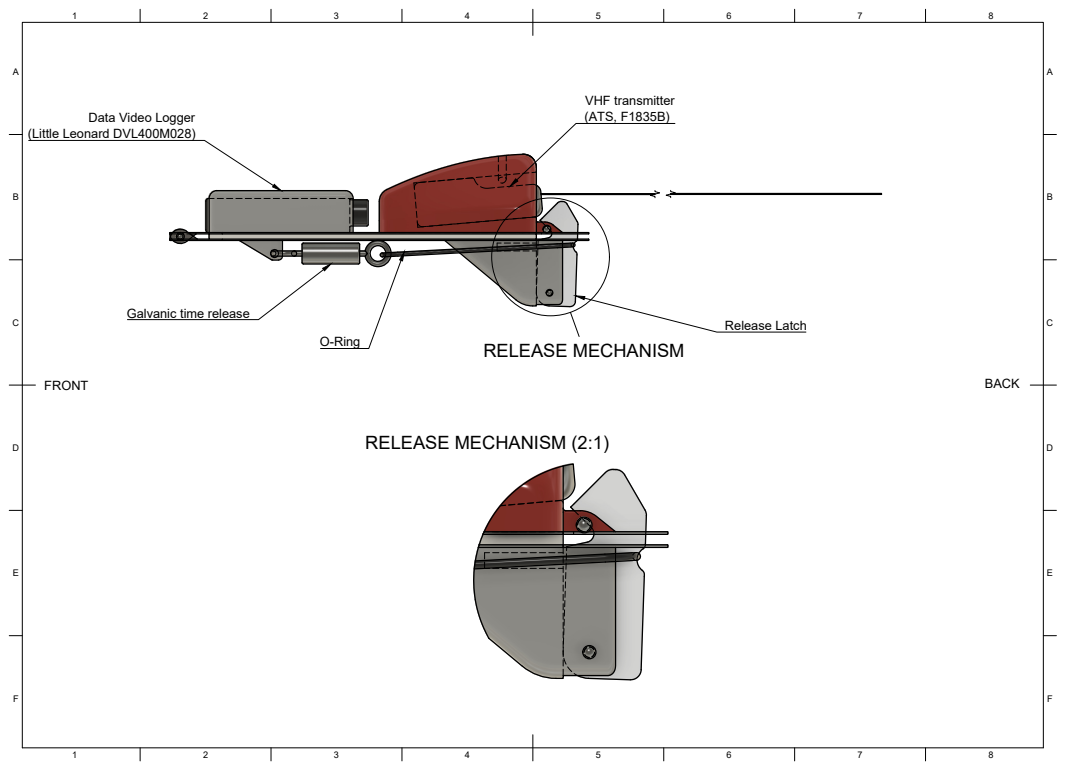
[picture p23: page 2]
(Little Leonard DVL400M028); VHF transmitter (ATS, F1835B); O-Ring; Release Latch; FRONT; BACK; RELEASE MECHANISM; RELEASE MECHANISM (2:1)

Data Video Logger

Galvanic time release

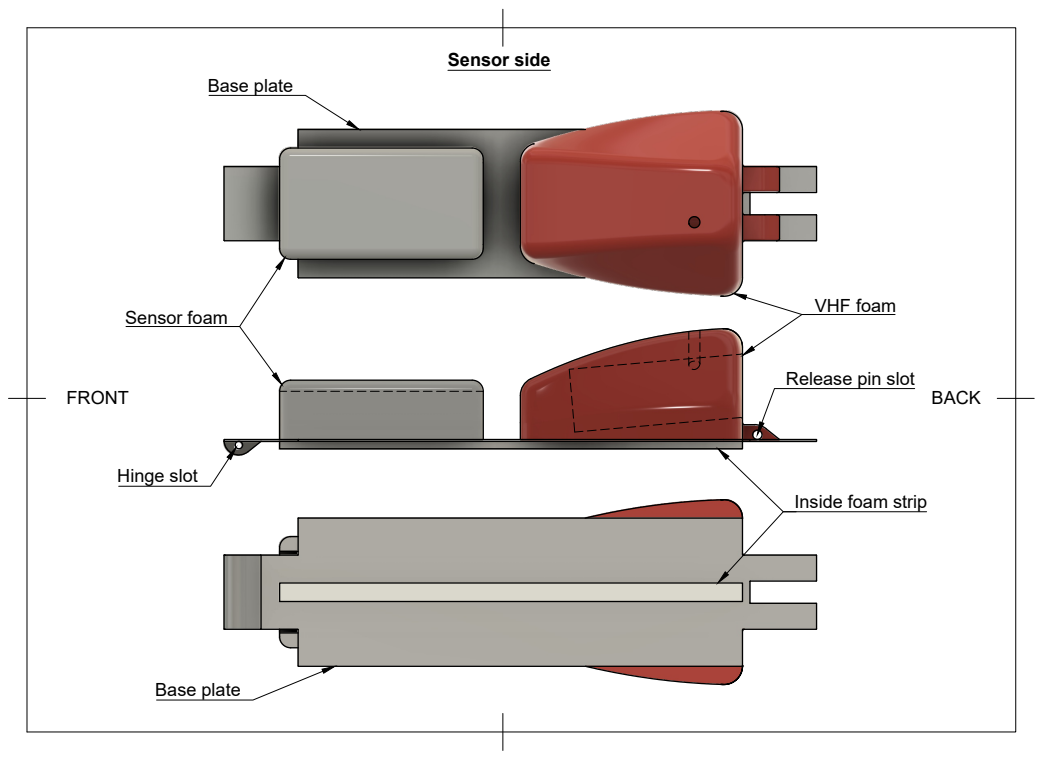
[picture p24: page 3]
FRONT; BACK; Hinge slot; Sensor side; Base plate

VHF foam Sensor foam

Release pin slot

Inside foam strip

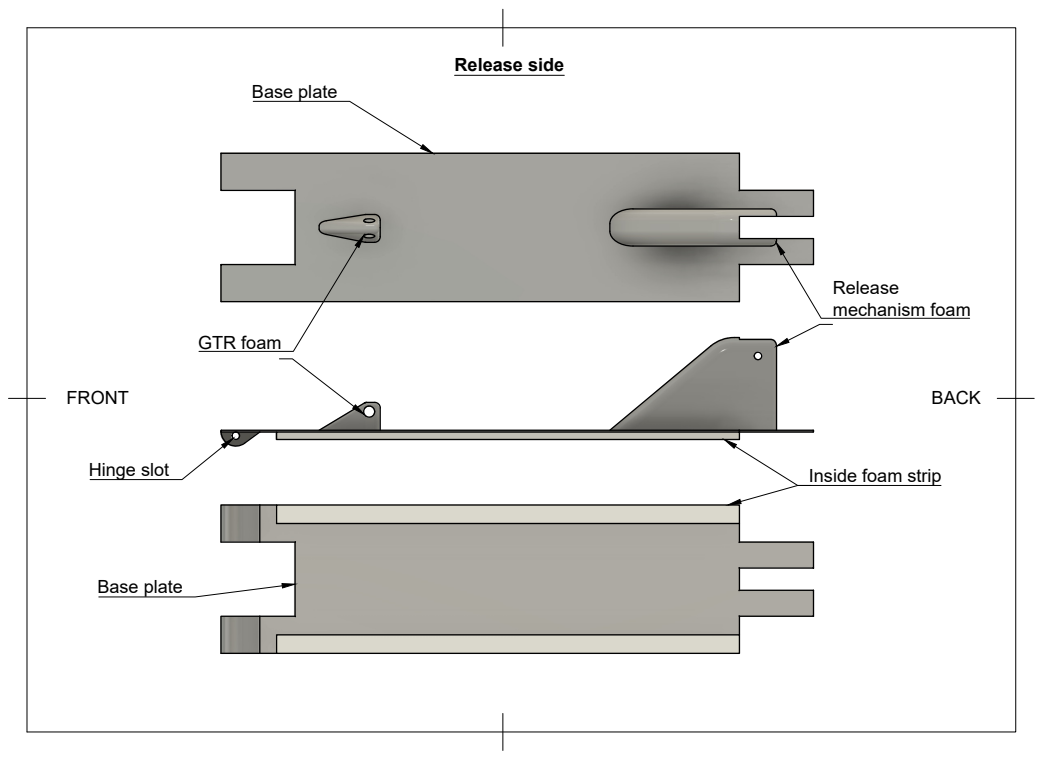
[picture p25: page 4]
FRONT; BACK; Release mechanism foam; GTR foam; Hinge slot; Inside foam strip; Release side; Base plate

Hinge | Inside foam strips

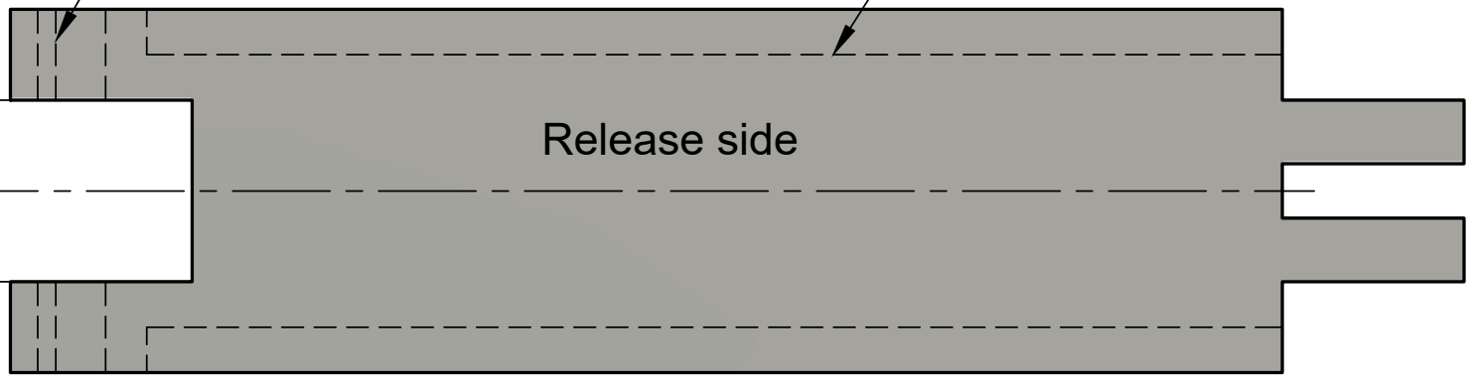
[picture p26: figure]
Release side
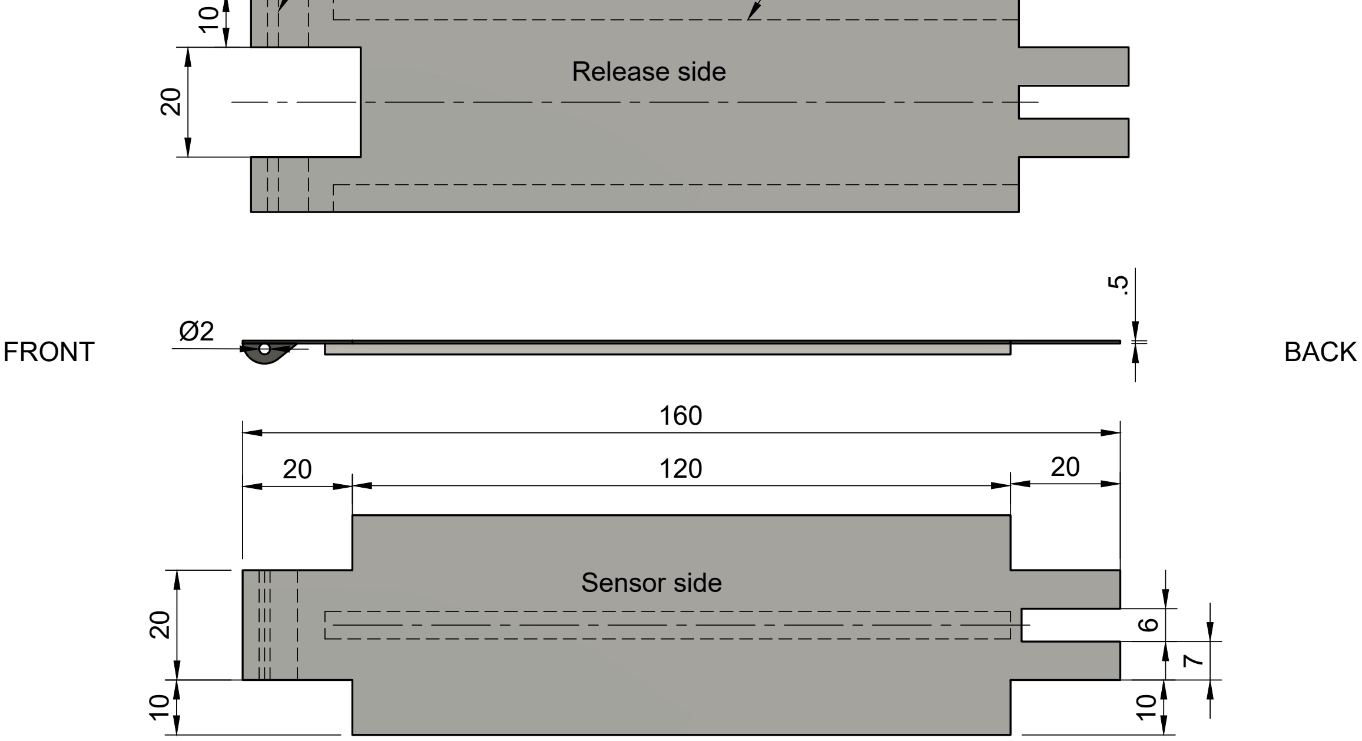
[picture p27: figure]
FRONT; BACK; Sensor side
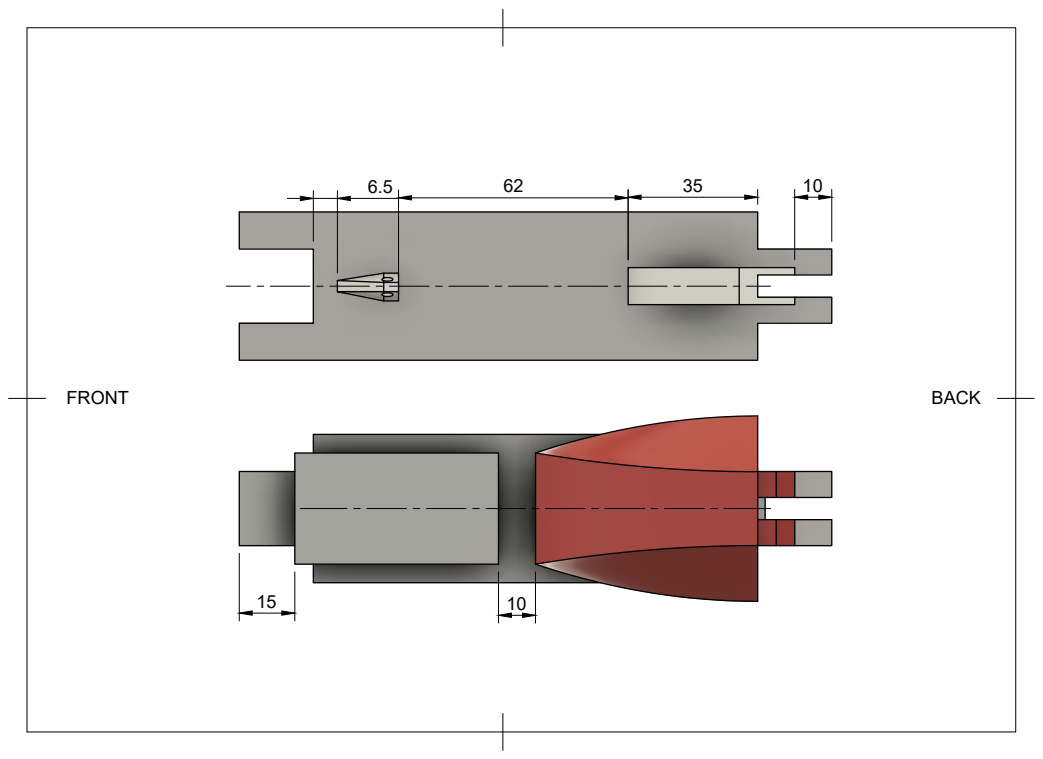
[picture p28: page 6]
FRONT; BACK
